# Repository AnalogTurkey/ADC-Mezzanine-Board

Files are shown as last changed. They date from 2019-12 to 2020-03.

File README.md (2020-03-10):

# ADC Mezzanine Board
 ADS7886 ADC Mezzanine Board for PHYS150
 
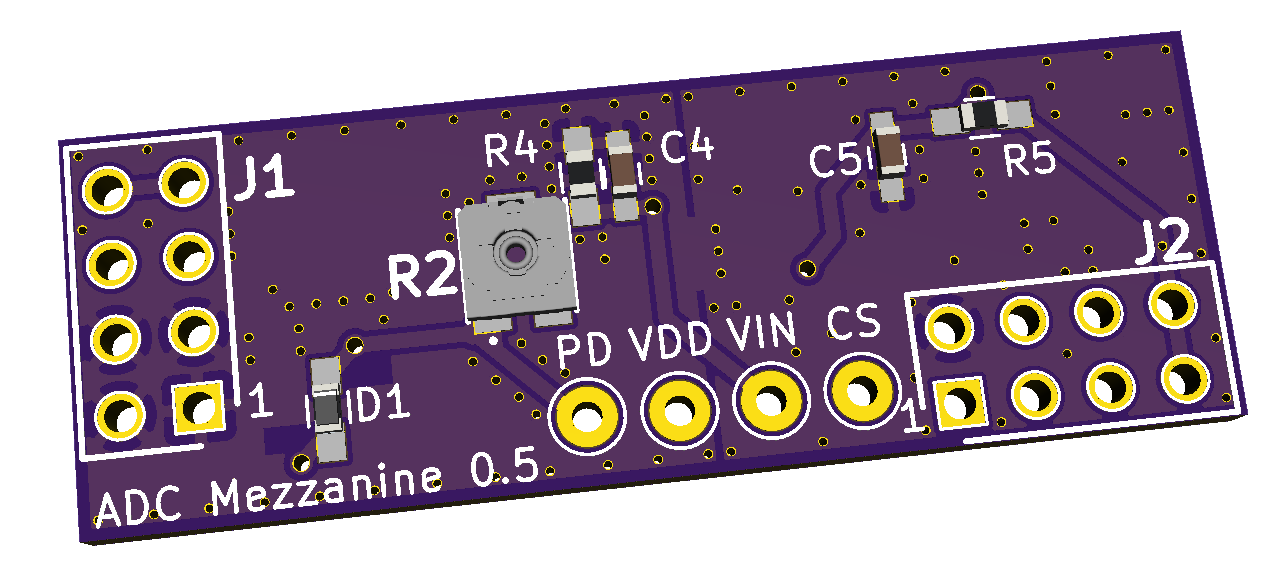
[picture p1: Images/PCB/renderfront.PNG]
Board Render
 

 KiCad PCB files are contained in the "ads7886_PCB" folder. If you do not have KiCad, see the "images" folder for the schematic and PCB. "ADC_Reader.py" is a basic python script for interfacing with the ADC board using a Raspberry Pi.
 
 ## The Hardware
 
The board has 4 main sections: power supply, analog input, digital input ("CS timing"), and ADC. 

#### Power Supply:
Power is regulated to 3.3V from the 5V board connectors. This circuit is about as boring as it gets. There isn't even a dedicated output capacitor on the LDO since the loads' decoupling capacitors are so close to the output.

#### Analog Input:
The ADC itself, under ideal conditions, is capped at 1 MSPS (million samples per second), which means that it is too slow to measure the entirety of a pulse. The board uses a peak detector to isolate the maximum voltage of a given event instead. 

**R2** is a 100Ω trimpot which stabilizes the op-amp and isolates it from the capacitive load. If this value is too low, the peak detector may oscillate and overshoot the actual value of the peak. If it is too high, the capacitor may not charge quickly enough and the peak detector will undershoot. An ideal value is around 10-20Ω, though you may want to adjust it using the scope. 

**R4** and **C4** form an RC decay. The given values, 1nF and 1MΩ, correspond to a time constant of 1ms. The value of R4 may be lowered to make the voltage decay more quickly. It is preferable to tweak **R4** rather than **C4** because the capacitive load may change the behavior of the op-amp and schottky diode.

#### Digital Input:
The latch signal from the main board is the output of a one-shot which is triggered every time the input signal exceeds a certain threshold. However, the ADC itself takes a measurement when its CS input transitions from high to low. The latch signal is inverted (to make it function like CS) and delayed using **R3** and **C5** (so that measurements are always taken *after* the peak has passed. This delay corresponds to roughly 250ns to fall from logical high to logical low using the given values.
 
#### The ADC:
The datasheet for the ADS7886 is available [here](http://www.ti.com/lit/ds/symlink/ads7886.pdf). 

#### Test Points
There are 4 test points on the board. **CS** is the chip select (trigger) input to the ADC. **Vin** is the analog input to the ADC, the voltage that is being measured. **PD** is across the trimpot from **Vin**; measuring accross these two points will give the value of **R2**. **VDD** is connected to the mezzanine board's 3.3V power supply.

 ## The Software

 This script listens for output data from the ADC and saves it to a file named "ADC_Data.txt".
 As is, connect SCLK to pin 13, HOLD to pin 7, and SDO to pin 11. On the Pi, navigate in the terminal to the directory the script is in, then run "python ADC_Reader.py". 
 
 The code only saves data to the file every once in a while since accessing the file takes a nontrivial amount of time. This can be changed by changing the value of "BufferSize" in the code.
 
 The code is heavily commented, so for finer details it's probably better to check there. 
 
 ## Images
 
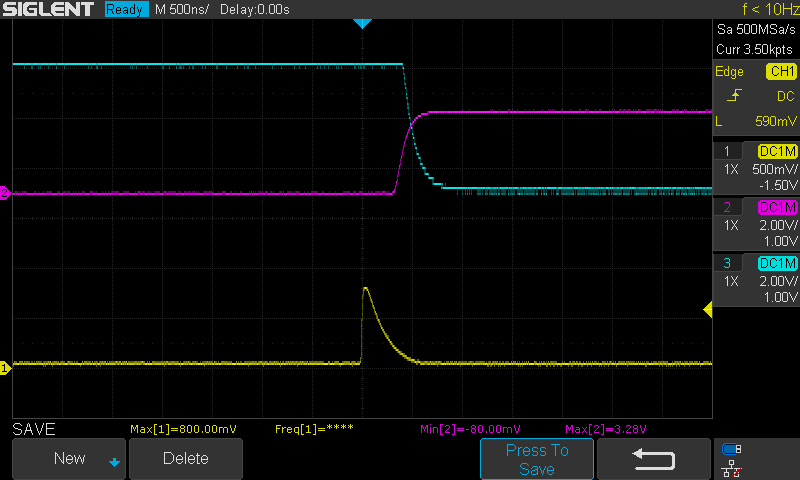
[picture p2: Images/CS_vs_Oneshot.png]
CS vs Oneshot
 
 
 In yellow is the raw signal. In purple is the 3.3V signal coming out of the Cosmic board's discriminator+oneshot. In cyan is the CS signal generated by the ADC: inverted, slightly RC-delayed, 5V.
 
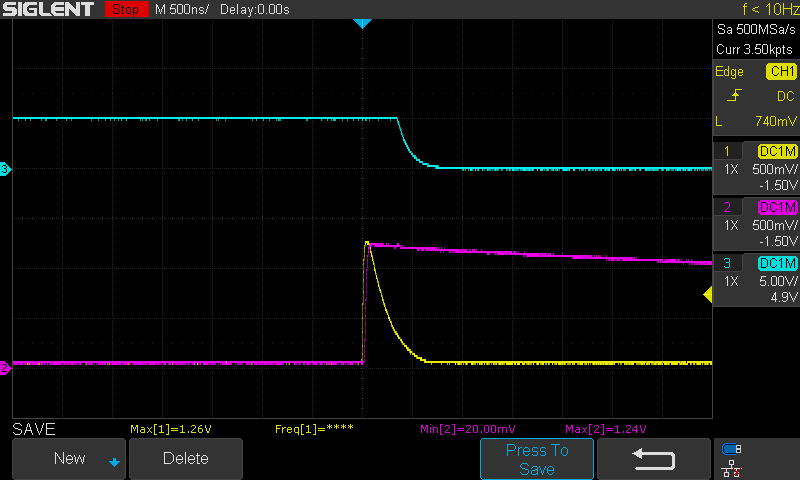
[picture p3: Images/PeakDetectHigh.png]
Peak Detect High
 
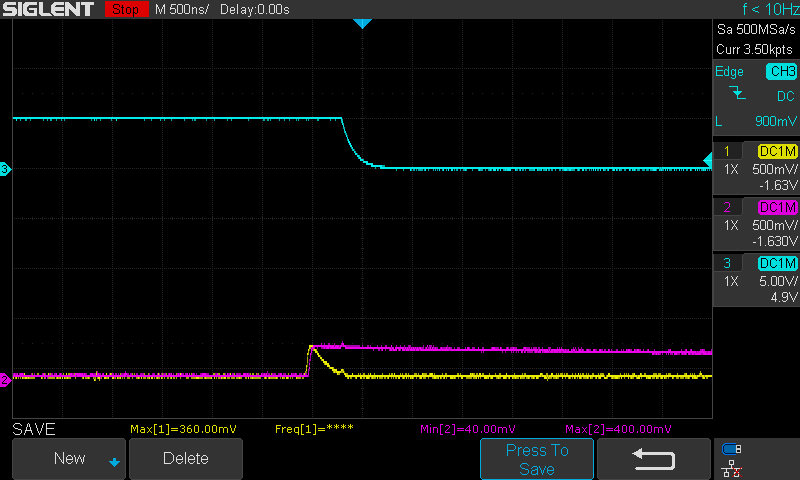
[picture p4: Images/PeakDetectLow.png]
Peak Detect Low
 
 
 The peak detector ever-so-slightly undershoots the peak, which is the most ideal response. These images were taken from a modified board with a peak detector time constant of 10µs. Somewhat interesting is the appearance of a small blip in the analog signals at the same time as the digital transition, implying that the supplies (or the grounds) could have been better isolated.
 
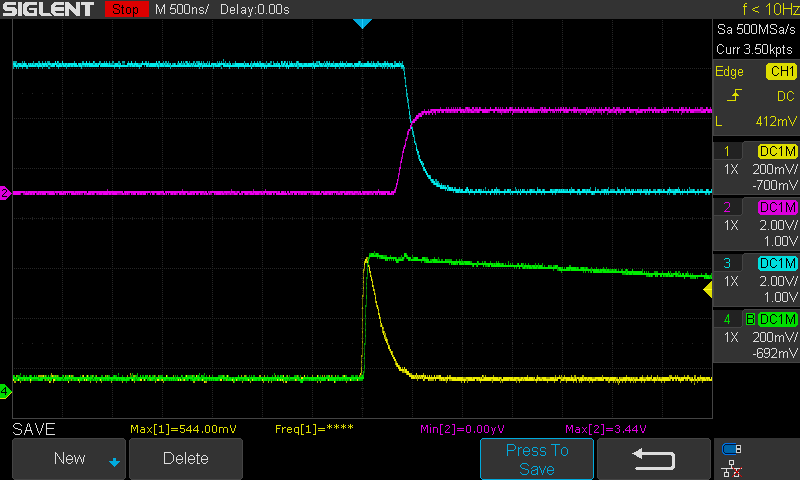
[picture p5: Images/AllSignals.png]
All Signals Together
 
 
 All of the above signals put together. Input signal in yellow, Peak Detector (test point VIN) in green, Oneshot in purple, CS in cyan.
 
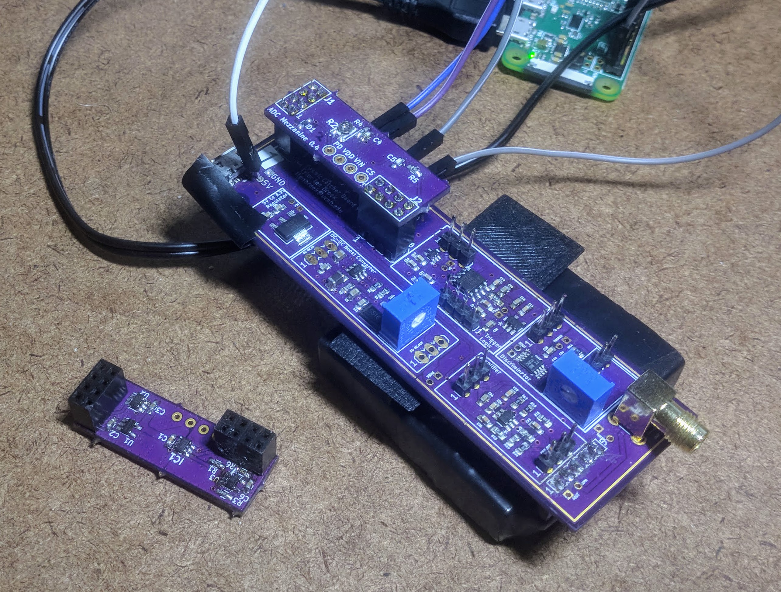
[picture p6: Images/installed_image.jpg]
Installed Board
 
 
 An ADC board installed, alongside another ADC board flipped upside down.

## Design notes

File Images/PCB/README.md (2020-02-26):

Some of the images attached here are currently for board version 0.4. Functionally there is minimal difference between this and 0.5; the only major change is that the "not connected" pin on the inverter has been grounded to make the board compatible with both the SN74LVC1G14 and SN74LVC1G240 inverters.

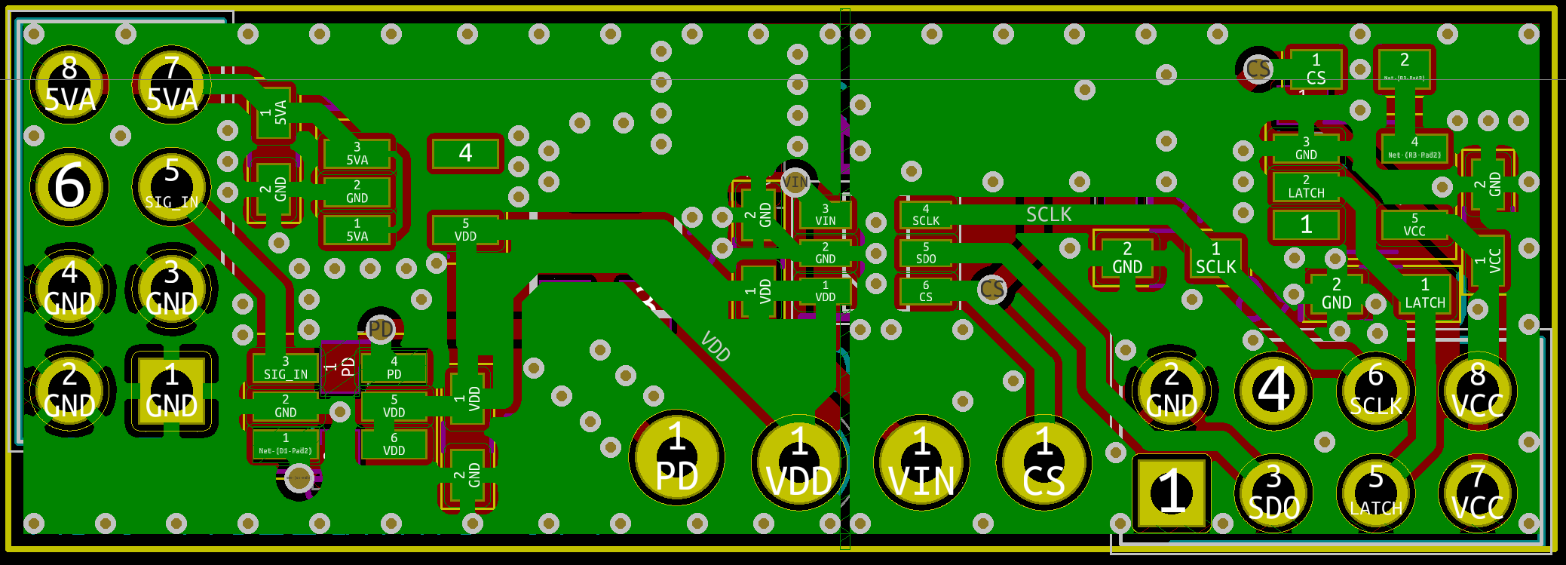
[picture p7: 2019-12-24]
Images/PCB/BCopper+pour.PNG

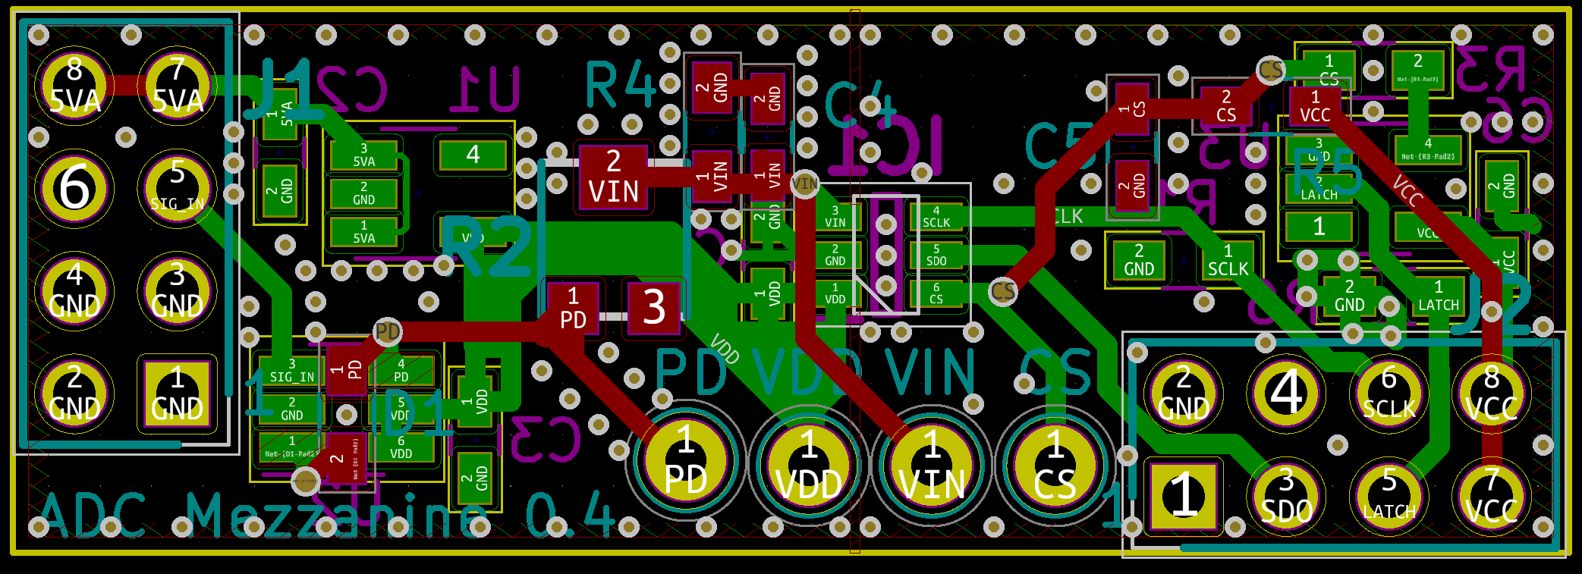
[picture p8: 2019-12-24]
Images/PCB/Copper.PNG

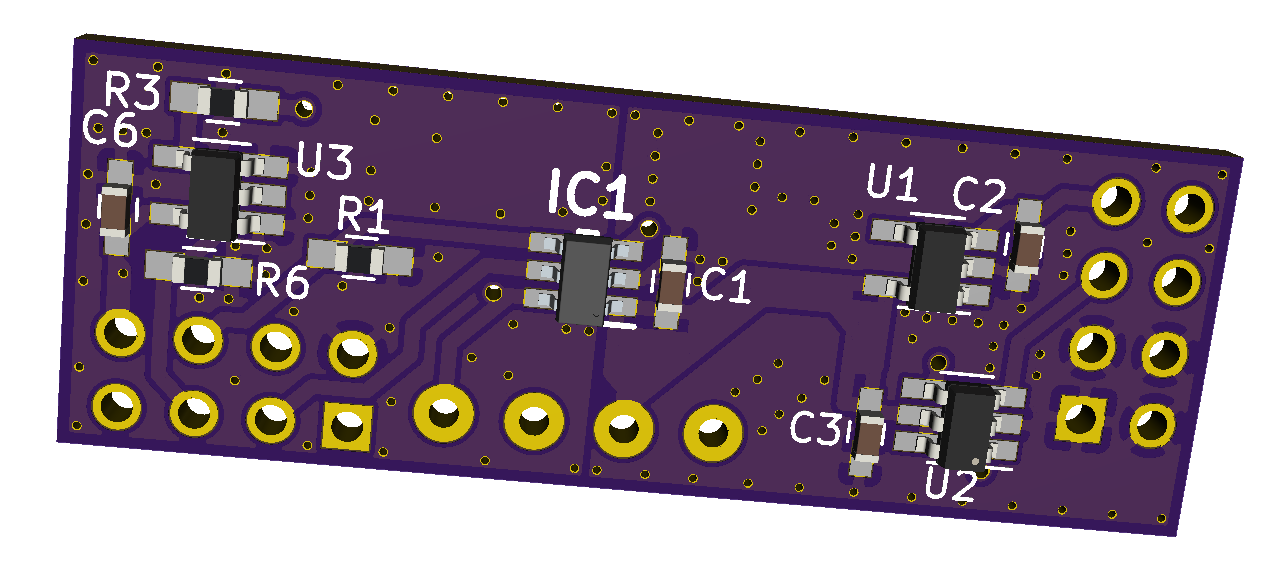
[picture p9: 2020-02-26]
Images/PCB/renderback.PNG

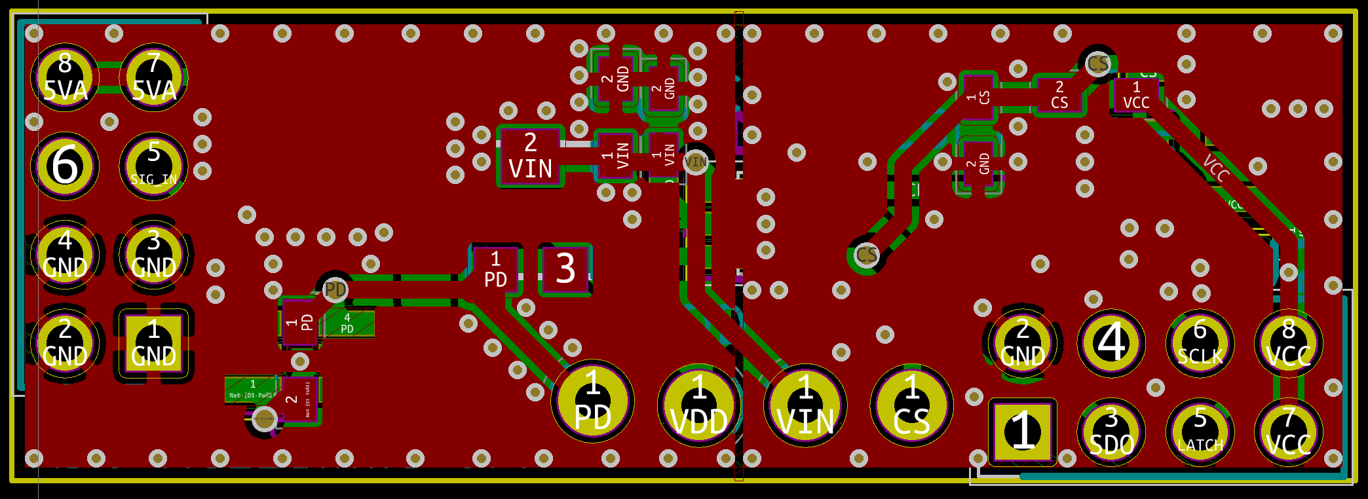
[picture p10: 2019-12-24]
Images/PCB/FCopper+pour.PNG

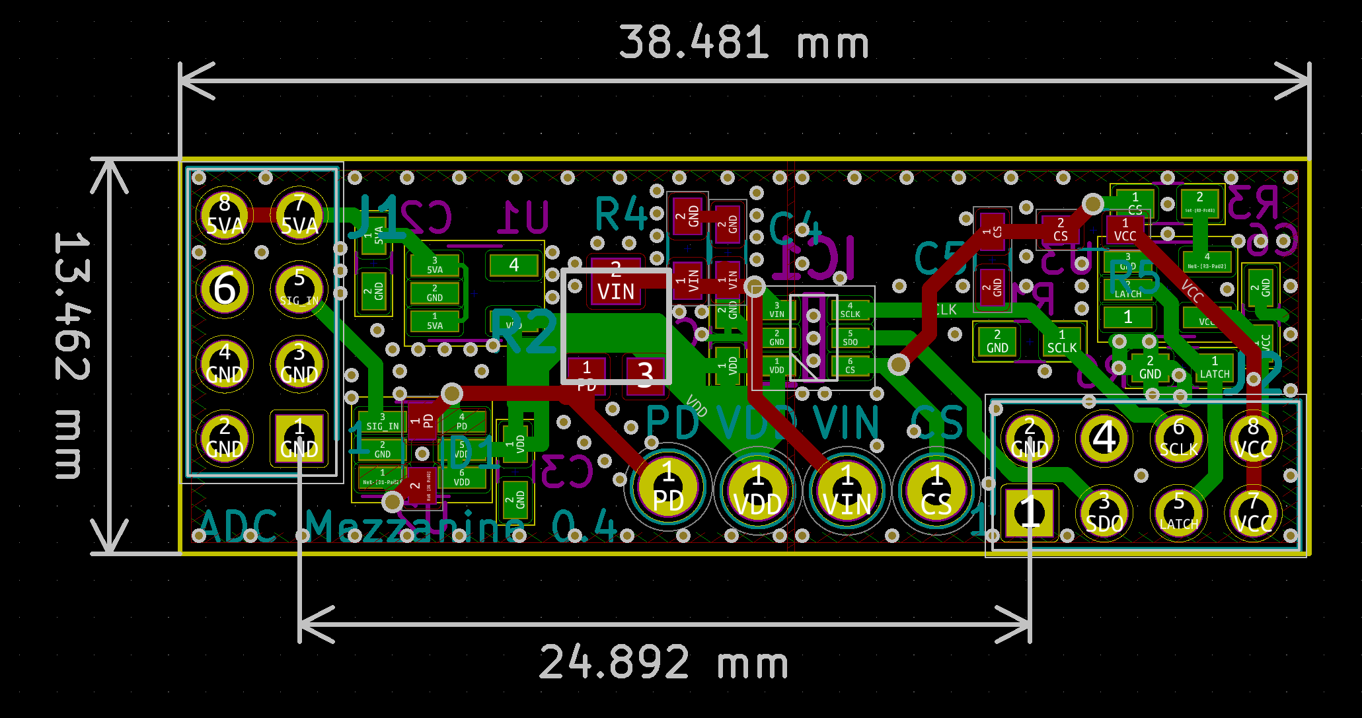
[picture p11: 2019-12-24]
Images/PCB/Copper+dims.PNG

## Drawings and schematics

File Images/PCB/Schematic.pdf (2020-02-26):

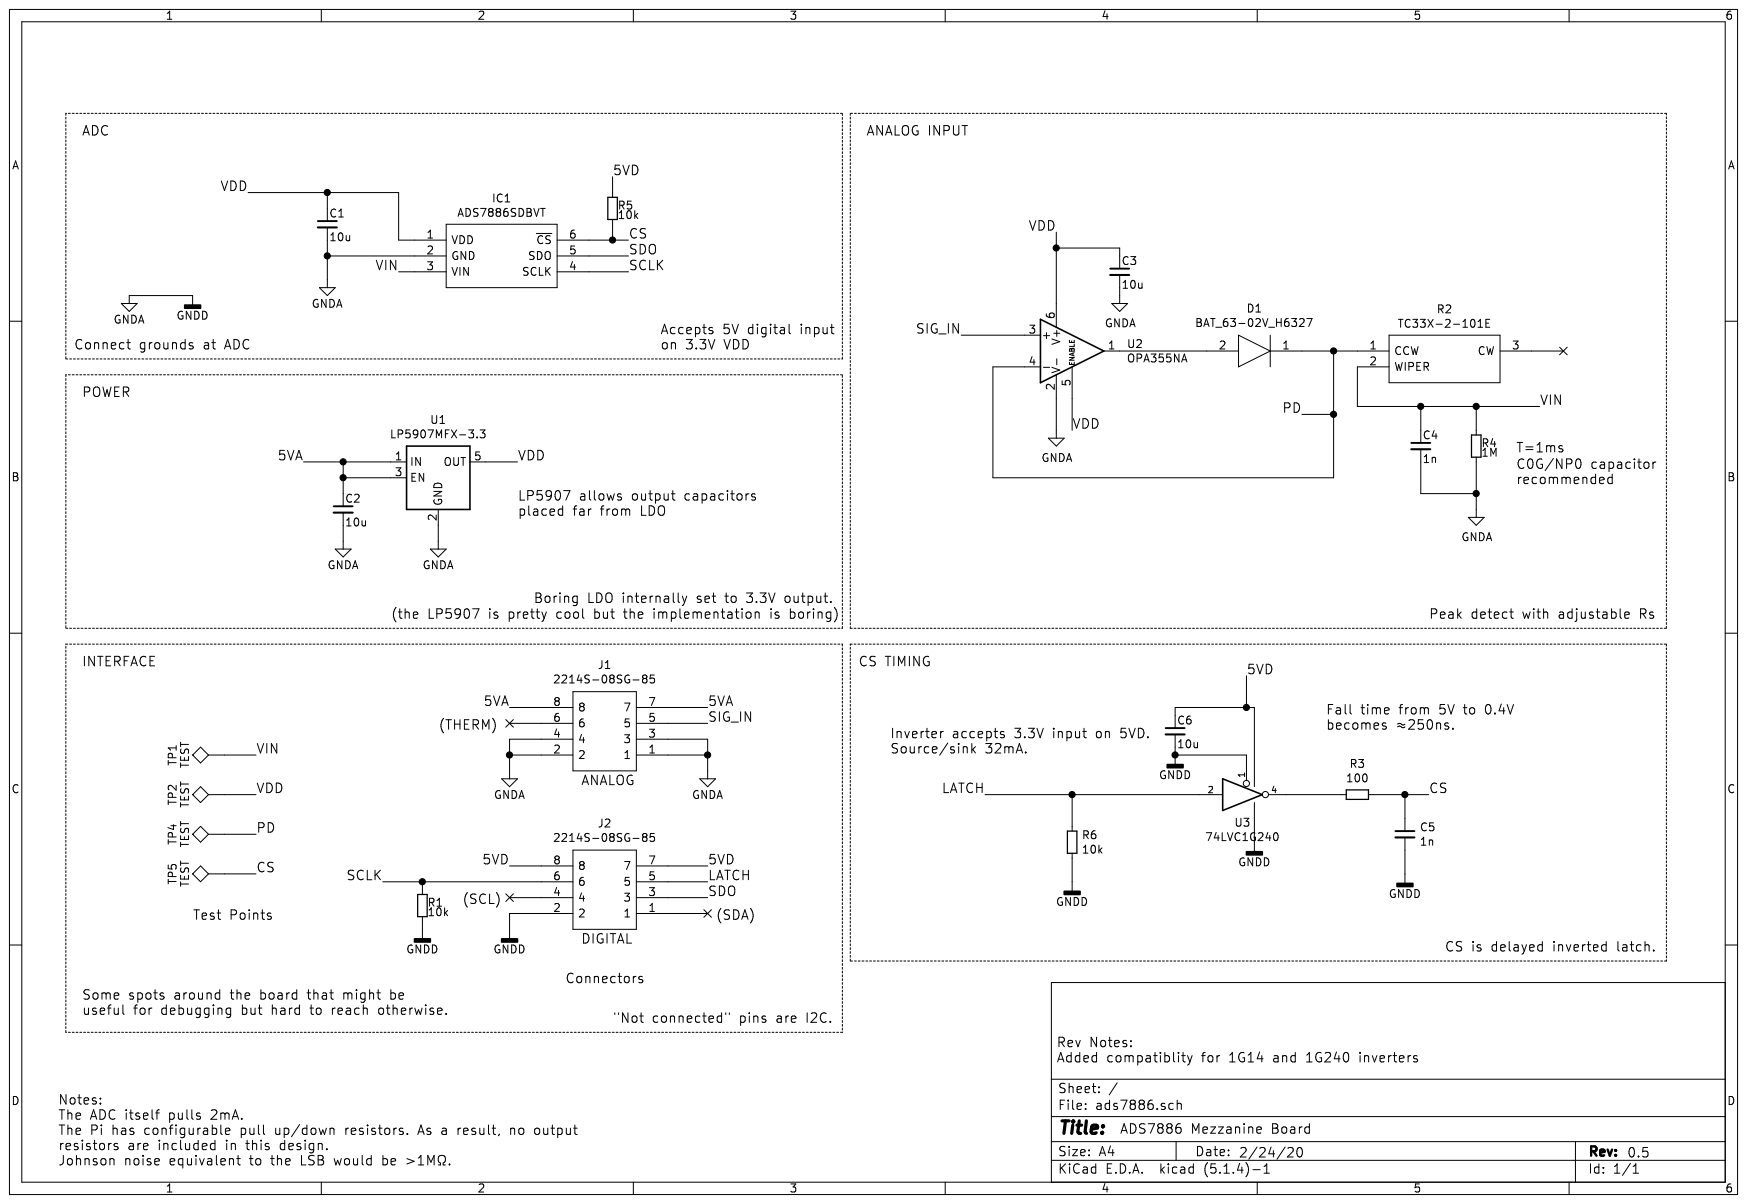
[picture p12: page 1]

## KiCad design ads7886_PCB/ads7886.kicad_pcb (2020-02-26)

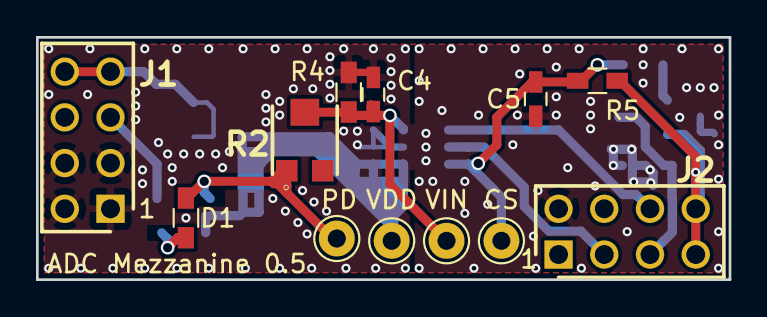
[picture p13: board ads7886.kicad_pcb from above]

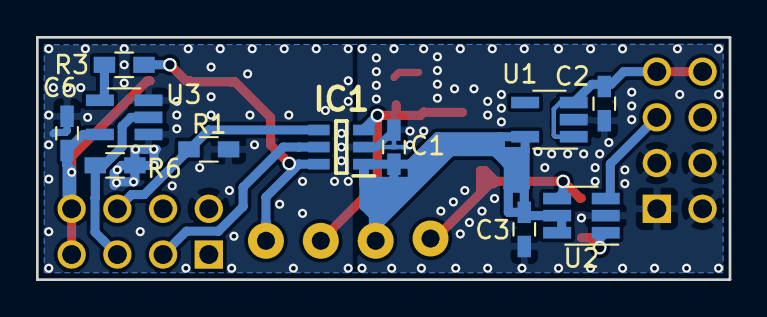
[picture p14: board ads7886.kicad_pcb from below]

Board: 2 copper layers, 38.5 x 13.5 mm, 23 parts (11 on the bottom side), 13 nets.

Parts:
C1, C2, C3, C6: 10u; C_0603_HandSoldering
C4, C5: 1n; C_0603_HandSoldering
CS: TEST; Pin_d1.0mm_L10.0mm
D1: BAT_63-02V_H6327; R_0603_HandSoldering
IC1: ADS7886SDBVT; SOT95P280X145-6N
J1, J2: 2214S-08SG-85; SHDR8W60P254_2X4_1016X508X850P
PD: TEST; Pin_d1.0mm_L10.0mm
R1, R5, R6: 10k; R_0603_HandSoldering
R2: TC33X-2-101E; TC33X-2_1
R3: 100; R_0603_HandSoldering
R4: 1M; R_0603_HandSoldering
U1: LP5907MFX-3.3; SOT-23-5_HandSoldering
U2: OPA355NA; SOT-23-6_Handsoldering
U3: 74LVC1G240; SOT-23-5_HandSoldering
VDD: TEST; Pin_d1.0mm_L10.0mm
VIN: TEST; Pin_d1.0mm_L10.0mm

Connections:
/5VA: C2.1, J1.7, J1.8, U1.1, U1.3
/CS: C5.1, CS.1, IC1.6, R3.1, R5.2
/LATCH: J2.5, R6.1, U3.2
/PD: D1.1, PD.1, R2.1, U2.4
/SCLK: IC1.4, J2.6, R1.1
/SDO: IC1.5, J2.3
/SIG_IN: J1.5, U2.3
/VDD: C1.1, C3.1, IC1.1, U1.5, U2.5, U2.6, VDD.1
/VIN: C4.1, IC1.3, R2.2, R4.1, VIN.1
GND: C1.2, C2.2, C3.2, C4.2, C5.2, C6.2, IC1.2, J1.1, J1.2, J1.3, J1.4, J2.2, R1.2, R4.2, R6.2, U1.2, U2.2, U3.1, U3.3
unnamed: D1.2, U2.1
unnamed: R3.2, U3.4
VCC: C6.1, J2.7, J2.8, R5.1, U3.5

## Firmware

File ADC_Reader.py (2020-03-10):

# -*- coding : utf8 -*-

# Datasheet for ADS7886: http://www.ti.com/lit/ds/symlink/ads7886.pdf

# Note that this signalling setup is pretty nonstandard. The ADC's CS is handled by the detector's latch. 
# Clock is only used to read out data and the sampling is handled by the peak detect and sample and hold.
# As a result, a slow clock can read data out quite slowly. This is easily bit-bangable as a result.
# Max toggle speed on GPIO in python is fairly low, far slower than the ADC's 20MHz limit;
# so no need to use delays after clock transitions before reading data.
# Send a clock signal at a reasonable-ish speed, wait for data. Read data manually. Repeat.

# Standards: Every method should end with SCLK high so no bits are accidentally skipped.

# Imports

import collections # for data structures
import time # for delays (if needed)
import RPi.GPIO as GPIO # to use the GPIO
from datetime import datetime # for timestamps. 

# Setting constants for the analog readings.

vref = 3300 # Reference voltage for ADC in mV
resolution = 12 # ADC resolution in bits (12 default)
threshold = 000 # minimum event voltage to record in mV (default 0). Setting a threshold in hardware is preferred.
bufferSize = 10 # Number of samples to store in buffer before saving to the file. 
# Lower values save measurements to file more often but will cause the code to run somewhat slower. 
# "1" immediately saves each sample as it arrives. 

# Preparing GPIO. 

# Enumerating pin numbers. Change these numbers to change the GPIO pin locations.
clockPin = 13
sdoPin = 11
holdPin = 7

# Configuring selected pins as GPIO
GPIO.setmode(GPIO.BOARD) # Pin numbers are based on the physical pin numbering.
GPIO.setwarnings(False)
GPIO.setup(holdPin, GPIO.OUT) # HOLD pin (keeps ADC chip select asserted until sampling is complete, to avoid unintentional shutdown).
GPIO.output(holdPin, GPIO.LOW) # Keep HOLD low for now since nothing is happening
GPIO.setup(clockPin, GPIO.OUT) # SCLK (clock) pin
GPIO.output(clockPin, GPIO.HIGH) #temporarily hold clock high because nothing can go wrong in that state
# SDO pin. The first 4 bits after a sample starts are all 0, so it's obvious where the data begins if this pin is pulled high.
GPIO.setup(sdoPin, GPIO.IN, pull_up_down=GPIO.PUD_UP) 
ADC_file = open ("ADC_file.txt", "a+") # Open the ADC file in append mode. Creates the file if it does not exist.
# This file is essentially comma-delimited; renaming to "ADC_file.csv" may make life easier.

# Since writing to file takes a few milliseconds, it makes sense to keep a buffer of measurements and write in batches.
dataBufferString = ("Starting a data run at " + datetime.now().strftime("%d %m %Y %H:%M:%S:%f") + "\n")

# Methods Follow Below.

# Method accounts for the ADC startup behavior. 
# The first sample read by the ADC after startup may be garbage data, so we need to ignore that.
def startADC(): 
    
    print('Starting ADC')

    waitForData() # run SCLK until SDO has data. This essentially throws away the questionable first data after startup.
        
    print('ADC started!')

# Method toggles SCLK until it detects the beginning of a data block (4 0's on SDO in a row). 
# The next bit read after running this method will be the first valid data bit.
def waitForData():

    # cycle SCLK to clear the ADC's buffer.
    i = 0
    while i < 16: 
        GPIO.output(clockPin, GPIO.LOW) # Falling edge of SCLK
        GPIO.output(clockPin, GPIO.HIGH) #Rising edge of SCLK
        i+=1
        if not(GPIO.input(sdoPin)): #if there are any 0's while doing this loop, the data block can't be read properly and the program should try clearing the buffer again.
            i = 0 # because python's for loops are <special>, it's easier to use a while with an iterable so the loop can be reset.

    dataDetected = False # Data not detected yet.
    while not dataDetected: # This loop terminates if it detects a 0 on SDO. Otherwise it continues looping.
        dataDetected = not(GPIO.input(sdoPin)) # If SDO is high, that means nothing is happening and there is no data.

    for i in range(3): #cycle through 3 remaining leading 0's. if any are not 0, return to waiting.
        GPIO.output(clockPin, GPIO.LOW) # Falling edge of SCLK
        GPIO.output(clockPin, GPIO.HIGH) 
        if GPIO.input(sdoPin): # if there are any 1's this is not a valid data block. Return to waiting.
            waitForData()
    
# Method waits for data then saves the ADC output (in mV) to a file.
def readADC():
    global dataBufferString # Yes, I know it's bad practice. 
    waitForData()
    
    GPIO.output(holdPin, GPIO.HIGH)
    startTime = datetime.now() # Keeps track of how long the sampling takes
    
    # Now to read the next 12 bits and save them to an array.
    validDataList = list(range(resolution))
    for i in validDataList:
        GPIO.output(clockPin, GPIO.LOW)
        GPIO.output(clockPin, GPIO.HIGH)
        validDataList[i] = GPIO.input(sdoPin)

    # At this point I have an array of 12 data bits. This needs to be converted to a number.    
    validData = int("".join(str(i) for i in validDataList),2) #convert to decimal
    # Convert number reading to a voltage in mV
    validData = (validData / (2.0 ** (resolution)-1)) * vref
  
    if (validData > threshold): # Sets a software voltage threshold for recording data
        print(str(validDataList)+str(validData)+" mV") # Print event to terminal
        
        # Calculate and display time elapsed during sampling
        timeElapsed = datetime.now() - startTime 
        print (str(timeElapsed.microseconds)+" microseconds taken")

        # saves format: timestamp, value in mV, time taken from hold asserted to hold deasserted        
        dataBufferString+=(datetime.now().strftime("%d %m %Y %H:%M:%S:%f") + ", " + str(validData) + ", " + str(timeElapsed.microseconds) + "\n")
        GPIO.output(holdPin, GPIO.LOW) #Sampling done, hold is released

    
# Main method. Running this alone should detect all ADC inputs and save them to the file.
def main():
    global dataBufferString

    startADC() # Discard the first ADC reading

    try:
        while True: # Record ADC readings until program is stopped.
            
            readADC()
            
            # Every <bufferSize> samples, save measurements to file
            if dataBufferString.count('\n') > bufferSize:  
                startTime = datetime.now()
                ADC_file.write(dataBufferString) # Save event and timestamp to file
                timeElapsed = datetime.now() - startTime
                print("Took " + str(timeElapsed.microseconds) + "microseconds to save " + str(bufferSize) + " samples to file")
                dataBufferString = ("Took " + str(timeElapsed.microseconds) + "microseconds to save " + str(bufferSize) + " samples to file \n")
            
    except:
         ADC_file.close()
         print("Done")
        
# Actually run the thing
main()

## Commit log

2019-12-24 Edited script, added readme
    Changed GPIO assignment in script, added readme and scope image.
    [ads7886.kicad_pcb, ads7886.sch]
2020-02-26 Improved PCB component compatilibity
    Widened LDO trace between IN and EN, mostly for aesthetics
    Grounded previously NC pad on inverter to allow for optional installation of 1G240 instead of 1G14
    [ads7886.kicad_pcb, ads7886.sch]
2020-02-26 Updated images and README
    Changed some PCB images to reflect new version, added scope shots and additional elaboration to readme.
    [ads7886.kicad_pcb]
2020-02-26 changed more extensions
    Oops, wrong case!
2020-03-10 Fixed Python Code
    Changed default pins (clock, sdo, hold) from 31, 33, 29 to 13, 11, 7 to make the code compatible with the standalone ADC Pi board. These values can be changed back in the python file on lines 33-35 i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
    Fixed an issue where the CS line going low after toggling SCLK and sampling SDO would cause the data to be offset by one bit, by monitoring SDO asynchronously until the data word begins.
